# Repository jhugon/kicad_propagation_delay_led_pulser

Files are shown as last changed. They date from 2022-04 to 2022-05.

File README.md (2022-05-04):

# Propagation Delay LED Pulser Board in KiCAD

This KiCad board pulses an LED with a very short pulse. The pulse width is
defined by the propagation delay of 3 inverters.

Main power supply: 5 V

LED bias: 0-1.4 V, lower is brighter

## Changelog

- v1.0 Difficult to hand-solder due to heat loss to ground plane (too many vias) and reversed 0612 capacitors
- v1.1 Remove extra vias and switch from 0612 to 1206 coupling caps

## Performance

### v1.1

Measured on 2022-05-04

Current draw not visible on power supply, so less than 10 mA

All measured with a 10x passive oscilloscope probe and ground clib hooked up to coax out:

- The clock coming out of the timer: 9.36 kHz
- The pulse coming out of the NAND gate:
  - Rise and fall times of 2 ns (may be probes)
  - Width of 11 ns
  - Baseline is 4.8 V
  - Pulse is 8 mV
- The pulse coming out of the coax driving inverters, going into R2:
  - A fair amount of ringing ~ 20%
  - Rise and fall times of 2 ns (see above)
  - Width of 11 ns
  - Baseline is -77 mV
  - Pulse is 5 V
- The LED anode:
  - Rise time: 2 ns
  - Fall time: ringing 8.5 ns
  - Width: 12 ns
  - Baseline: -77 mV
  - Pulse: 2.8 V

Pulse measurement of coax output into high-Z scope input:

- Rise time 2.48 ns
- Fall time 2.45 ns
- Width 11.61 ns
- Baseline -90 mV
- Pulse 4.6 V
- Ringing ~ 10%, damped out around 20 ns after pulse fall

LED pulse measurements return a signal as expected at 9.36 kHz. The signal is
controllable with the bias voltage. Noise seems high, but that may be something
else

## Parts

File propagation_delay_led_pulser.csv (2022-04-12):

Source: | /home/jhugon/kicad/propagation_delay_led_pulser/propagation_delay_led_pulser.kicad_sch
Date: | Tue 12 Apr 2022 01:35:03 PM CDT
Tool: | Eeschema 6.0.4-6f826c9f35~116~ubuntu20.04.1
Generator: | /usr/share/kicad/plugins/bom_csv_grouped_by_value.py
Component Count: | 15
Individual Components:
Item | Qty | Reference(s) | Value | LibPart | Footprint | Datasheet | Mfr | Part
 |  | C1 | 22u | Device:C | Capacitor_SMD:C_1206_3216Metric_Pad1.33x1.80mm_HandSolder | https://www.mouser.com/datasheet/2/585/MLCC-1837944.pdf | Samsung | CL31A226KAHNNNE
 |  | C2 | 1n | Device:C | Capacitor_SMD:C_1206_3216Metric_Pad1.33x1.80mm_HandSolder | https://www.mouser.com/datasheet/2/40/C0GNP0_Dielectric-951274.pdf | Kyocera AVX | 12063A102FAT2A
 |  | C3 | 0.1u | Device:C | Capacitor_SMD:C_1206_3216Metric_Pad1.33x1.80mm_HandSolder | https://www.mouser.com/datasheet/2/585/MLCC-1837944.pdf | Samsung | CL31B104KBCNNND
 |  | C4 | 0.1u | Device:C | Capacitor_SMD:C_1206_3216Metric_Pad1.33x1.80mm_HandSolder | https://www.mouser.com/datasheet/2/585/MLCC-1837944.pdf | Samsung | CL31B104KBCNNND
 |  | C5 | 0.1u | Device:C | Capacitor_SMD:C_1206_3216Metric_Pad1.33x1.80mm_HandSolder | https://www.mouser.com/datasheet/2/585/MLCC-1837944.pdf | Samsung | CL31B104KBCNNND
 |  | C6 | 1u | Device:C | Capacitor_SMD:C_1206_3216Metric_Pad1.33x1.80mm_HandSolder | https://www.mouser.com/datasheet/2/585/MLCC-1837944.pdf | Samsung | CL31B105KBHNFNE
 |  | D1 | LED | Device:LED | LED_SMD:LED_1206_3216Metric_Pad1.42x1.75mm_HandSolder | https://www.mouser.com/datasheet/2/239/Lite-On-LTST-C150TBKT-1175371.pdf | Lite-On | LTST-C150TBKT
 |  | J1 | Power/Bias In | Connector_Generic:Conn_02x02_Top_Bottom | Connector_Molex:Molex_Nano-Fit_105314-xx04_2x02_P2.50mm_Horizontal | https://www.mouser.com/datasheet/2/276/4/1053141304_PCB_HEADERS-2883302.pdf | Molex | 1053141304
 |  | J2 | Pulse Out | Connector:Conn_Coaxial | Connector_Coaxial:SMA_Amphenol_132289_EdgeMount | https://www.mouser.com/datasheet/2/18/1/amphs06501_1-2259276.pdf | Amphenol RF | 132289
 |  | R1 | 72K | Device:R_US | Resistor_SMD:R_1206_3216Metric_Pad1.30x1.75mm_HandSolder | https://www.mouser.com/datasheet/2/427/dcrcwe3-1762152.pdf | Vishay | CRCW120671K5FKEA
 |  | R2 | 50R | Device:R_US | Resistor_SMD:R_1206_3216Metric_Pad1.30x1.75mm_HandSolder | https://www.mouser.com/datasheet/2/427/crcwce3-1762584.pdf | Vishay | CRCW120649R9FKEAC
 |  | R3 | 50R | Device:R_US | Resistor_SMD:R_1206_3216Metric_Pad1.30x1.75mm_HandSolder | https://www.mouser.com/datasheet/2/427/crcwce3-1762584.pdf | Vishay | CRCW120649R9FKEAC
 |  | U1 | 74AC14 | 74xx:74HC14 | Package_SO:SOIC-14_3.9x8.7mm_P1.27mm | https://www.ti.com/lit/ds/symlink/sn74ac14.pdf | Texas Instruments | SN74AC14D
 |  | U2 | ICM7555xB | Timer:ICM7555xB | Package_SO:SOIC-8_3.9x4.9mm_P1.27mm | http://www.intersil.com/content/dam/Intersil/documents/icm7/icm7555-56.pdf | Maxim | ICM7555ESA+
 |  | U3 | 74AHC1G00 | 74xGxx:74AHC1G00 | Package_TO_SOT_SMD:SOT-23-5_HandSoldering | http://www.ti.com/lit/sg/scyt129e/scyt129e.pdf | Texas Instruments | SN74AHC1G00DBV
Collated Components:
Item | Qty | Reference(s) | Value | LibPart | Footprint | Datasheet | Mfr | Part
1 | 1 | C1 | 22u | Device:C | Capacitor_SMD:C_1206_3216Metric_Pad1.33x1.80mm_HandSolder | https://www.mouser.com/datasheet/2/585/MLCC-1837944.pdf | Samsung | CL31A226KAHNNNE
2 | 1 | C2 | 1n | Device:C | Capacitor_SMD:C_1206_3216Metric_Pad1.33x1.80mm_HandSolder | https://www.mouser.com/datasheet/2/40/C0GNP0_Dielectric-951274.pdf | Kyocera AVX | 12063A102FAT2A
3 | 3 | C3, C4, C5 | 0.1u | Device:C | Capacitor_SMD:C_1206_3216Metric_Pad1.33x1.80mm_HandSolder | https://www.mouser.com/datasheet/2/585/MLCC-1837944.pdf | Samsung | CL31B104KBCNNND
4 | 1 | C6 | 1u | Device:C | Capacitor_SMD:C_1206_3216Metric_Pad1.33x1.80mm_HandSolder | https://www.mouser.com/datasheet/2/585/MLCC-1837944.pdf | Samsung | CL31B105KBHNFNE
5 | 1 | D1 | LED | Device:LED | LED_SMD:LED_1206_3216Metric_Pad1.42x1.75mm_HandSolder | https://www.mouser.com/datasheet/2/239/Lite-On-LTST-C150TBKT-1175371.pdf | Lite-On | LTST-C150TBKT
6 | 1 | J1 | Power/Bias In | Connector_Generic:Conn_02x02_Top_Bottom | Connector_Molex:Molex_Nano-Fit_105314-xx04_2x02_P2.50mm_Horizontal | https://www.mouser.com/datasheet/2/276/4/1053141304_PCB_HEADERS-2883302.pdf | Molex | 1053141304
7 | 1 | J2 | Pulse Out | Connector:Conn_Coaxial | Connector_Coaxial:SMA_Amphenol_132289_EdgeMount | https://www.mouser.com/datasheet/2/18/1/amphs06501_1-2259276.pdf | Amphenol RF | 132289
8 | 1 | R1 | 72K | Device:R_US | Resistor_SMD:R_1206_3216Metric_Pad1.30x1.75mm_HandSolder | https://www.mouser.com/datasheet/2/427/dcrcwe3-1762152.pdf | Vishay | CRCW120671K5FKEA
9 | 2 | R2, R3 | 50R | Device:R_US | Resistor_SMD:R_1206_3216Metric_Pad1.30x1.75mm_HandSolder | https://www.mouser.com/datasheet/2/427/crcwce3-1762584.pdf | Vishay | CRCW120649R9FKEAC
10 | 1 | U1 | 74AC14 | 74xx:74HC14 | Package_SO:SOIC-14_3.9x8.7mm_P1.27mm | https://www.ti.com/lit/ds/symlink/sn74ac14.pdf | Texas Instruments | SN74AC14D
11 | 1 | U2 | ICM7555xB | Timer:ICM7555xB | Package_SO:SOIC-8_3.9x4.9mm_P1.27mm | http://www.intersil.com/content/dam/Intersil/documents/icm7/icm7555-56.pdf | Maxim | ICM7555ESA+
12 | 1 | U3 | 74AHC1G00 | 74xGxx:74AHC1G00 | Package_TO_SOT_SMD:SOT-23-5_HandSoldering | http://www.ti.com/lit/sg/scyt129e/scyt129e.pdf | Texas Instruments | SN74AHC1G00DBV

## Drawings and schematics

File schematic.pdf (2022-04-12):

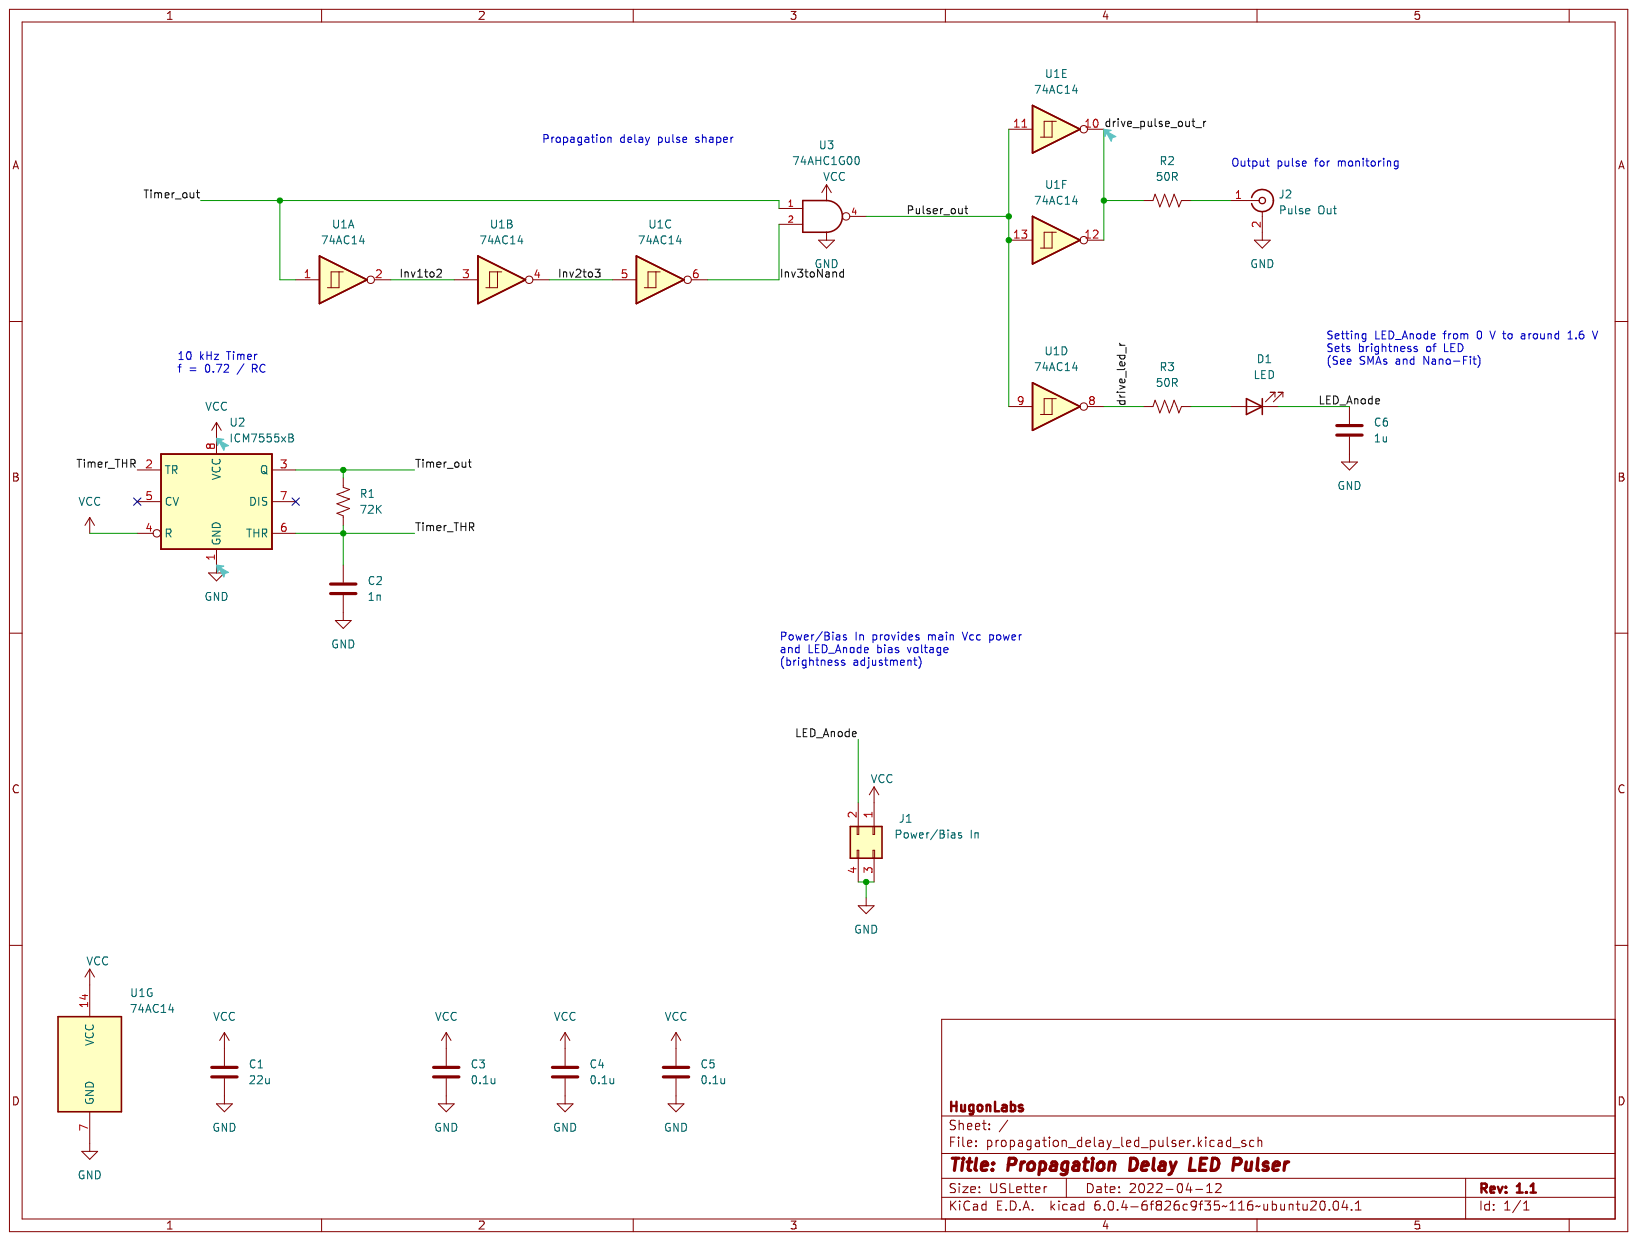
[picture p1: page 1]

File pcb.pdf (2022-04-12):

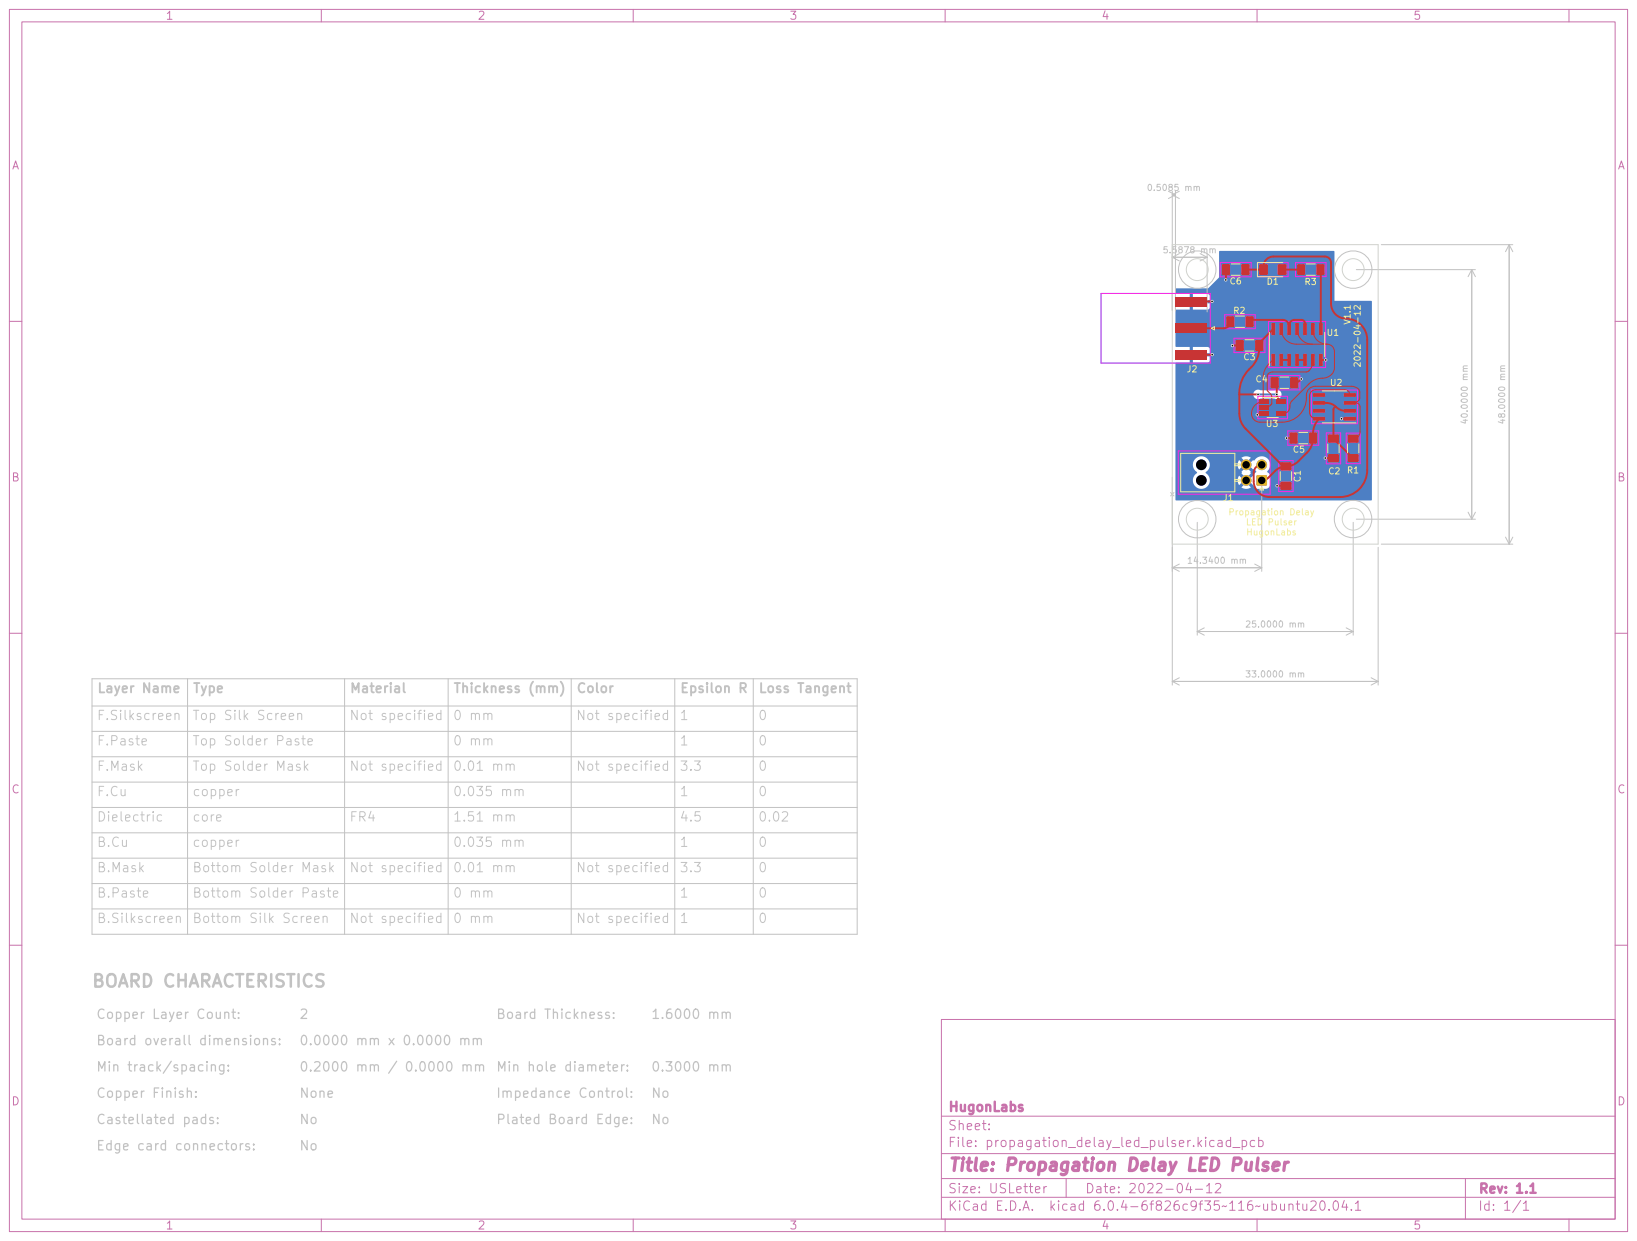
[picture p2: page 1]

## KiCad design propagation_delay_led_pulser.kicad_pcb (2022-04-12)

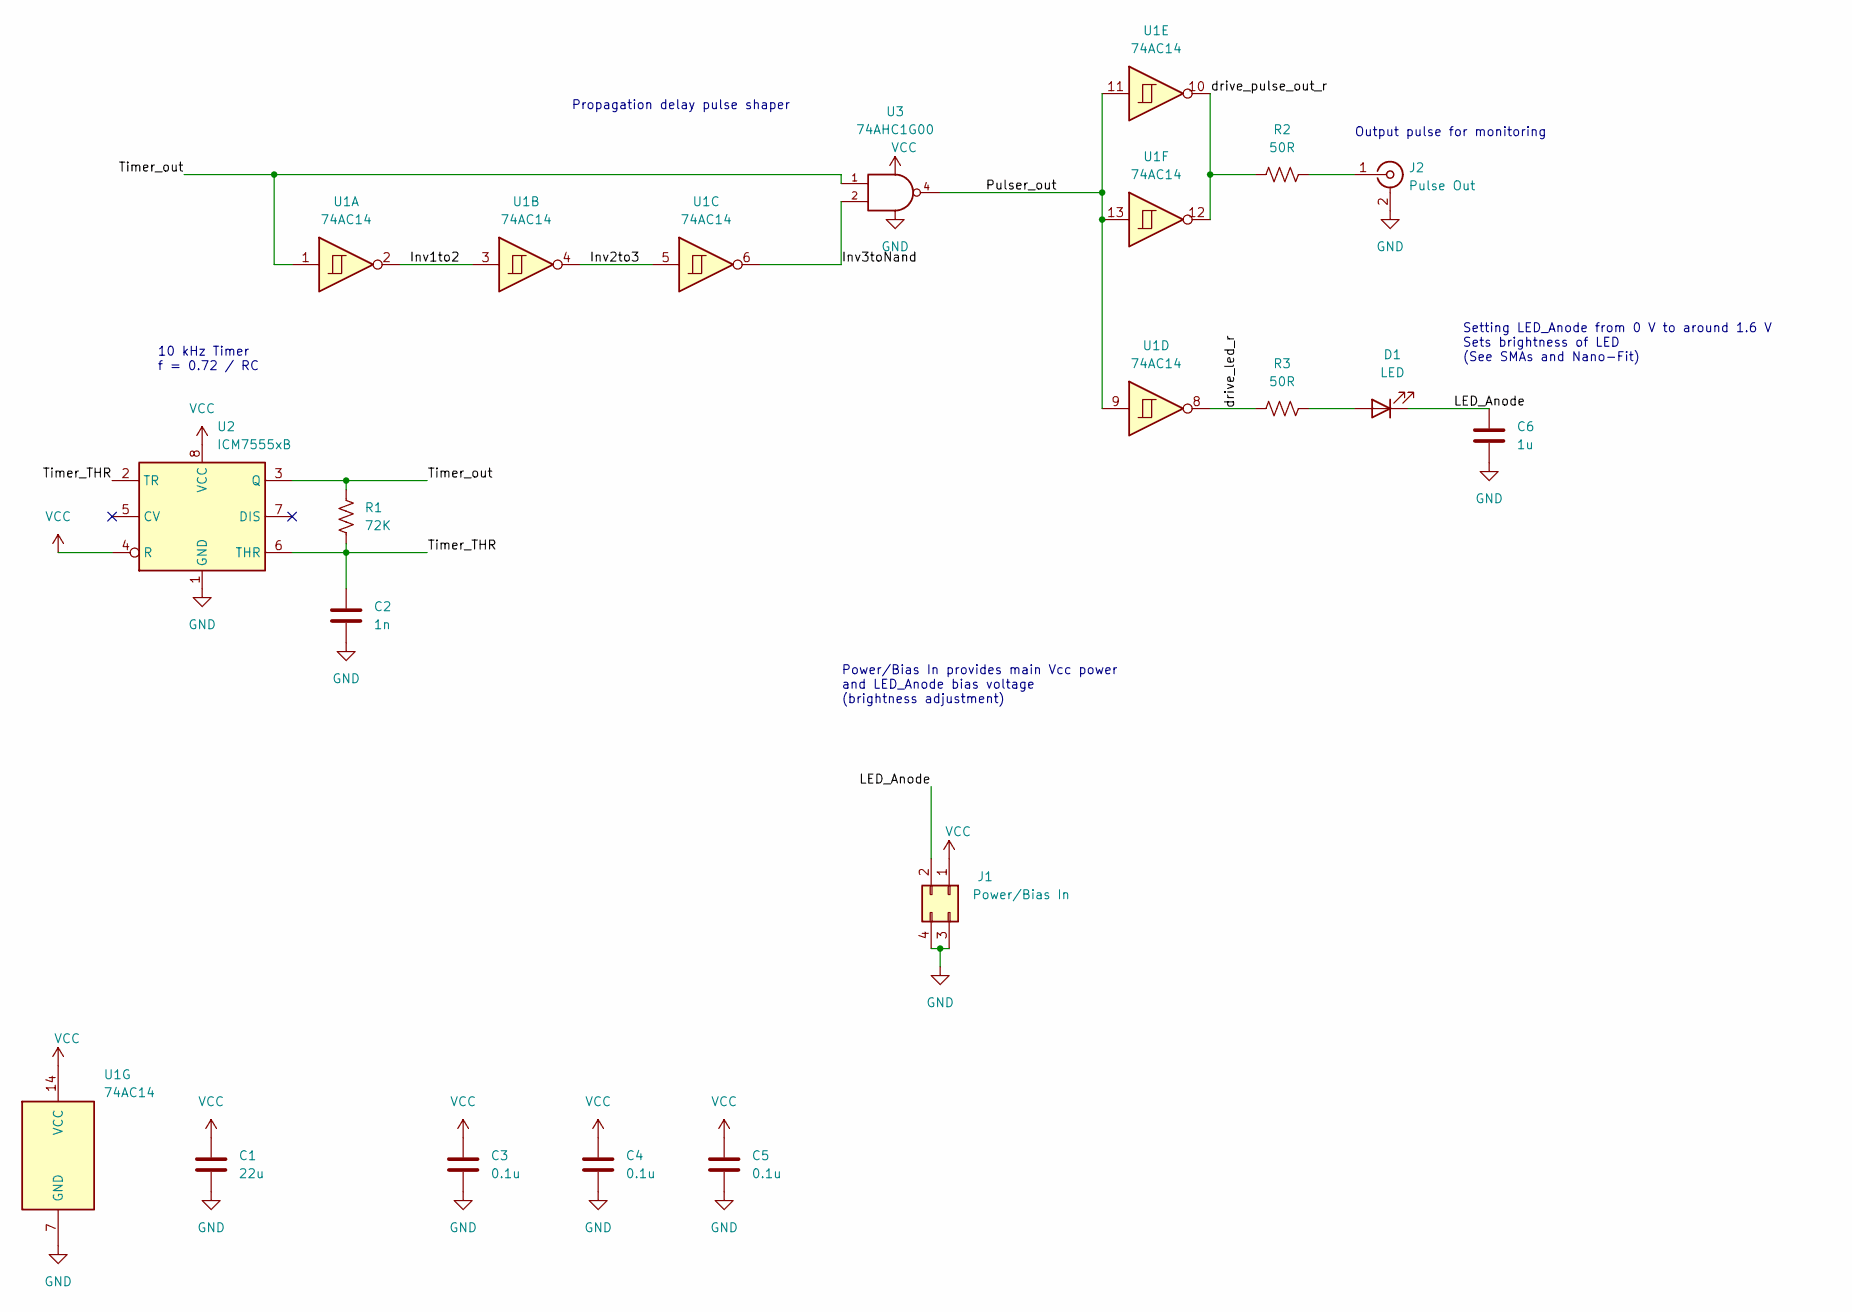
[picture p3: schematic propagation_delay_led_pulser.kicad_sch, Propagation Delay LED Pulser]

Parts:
C1: 22u; C_1206_3216Metric_Pad1.33x1.80mm_HandSolder; Part CL31A226KAHNNNE
C2: 1n; C_1206_3216Metric_Pad1.33x1.80mm_HandSolder; Part 12063A102FAT2A
C3, C4, C5: 0.1u; C_1206_3216Metric_Pad1.33x1.80mm_HandSolder; Part CL31B104KBCNNND
C6: 1u; C_1206_3216Metric_Pad1.33x1.80mm_HandSolder; Part CL31B105KBHNFNE
D1: LED; LED_1206_3216Metric_Pad1.42x1.75mm_HandSolder; Part LTST-C150TBKT
J1: Power/Bias In; Molex_Nano-Fit_105314-xx04_2x02_P2.50mm_Horizontal; Part 1053141304
J2: Pulse Out; SMA_Amphenol_132289_EdgeMount; Part 132289
R1: 72K; R_1206_3216Metric_Pad1.30x1.75mm_HandSolder; Part CRCW120671K5FKEA
R2, R3: 50R; R_1206_3216Metric_Pad1.30x1.75mm_HandSolder; Part CRCW120649R9FKEAC
U1: 74AC14; SOIC-14_3.9x8.7mm_P1.27mm; Part SN74AC14D
U2: ICM7555xB; SOIC-8_3.9x4.9mm_P1.27mm; Part ICM7555ESA+
U3: 74AHC1G00; SOT-23-5_HandSoldering; Part SN74AHC1G00DBV

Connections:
/Inv1to2: U1.2, U1.3
/Inv2to3: U1.4, U1.5
/Inv3toNand: U1.6, U3.2
/LED_Anode: C6.1, D1.1 (K), J1.2
/Pulser_out: U1.9, U1.11, U1.13, U3.4
/Timer_THR: C2.1, R1.2, U2.2 (TR), U2.6 (THR)
/Timer_out: R1.1, U1.1, U2.3 (Q), U3.1
/drive_led_r: R3.1, U1.8
/drive_pulse_out_r: R2.1, U1.10, U1.12
GND: C1.2, C2.2, C3.2, C4.2, C5.2, C6.2, J1.3, J1.4, J2.2 (Ext), U1.7 (GND), U2.1 (GND), U3.3 (GND)
unnamed: D1.2 (A), R3.2
unnamed: J2.1 (In), R2.2
VCC: C1.1, C3.1, C4.1, C5.1, J1.1, U1.14 (VCC), U2.4 (R), U2.8 (VCC), U3.5 (VCC)

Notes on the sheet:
Output pulse for monitoring
Setting LED_Anode from 0 V to around 1.6 V Sets brightness of LED (See SMAs and Nano-Fit)
Propagation delay pulse shaper
10 kHz Timer f = 0.72 / RC
Power/Bias In provides main Vcc power and LED_Anode bias voltage (brightness adjustment)

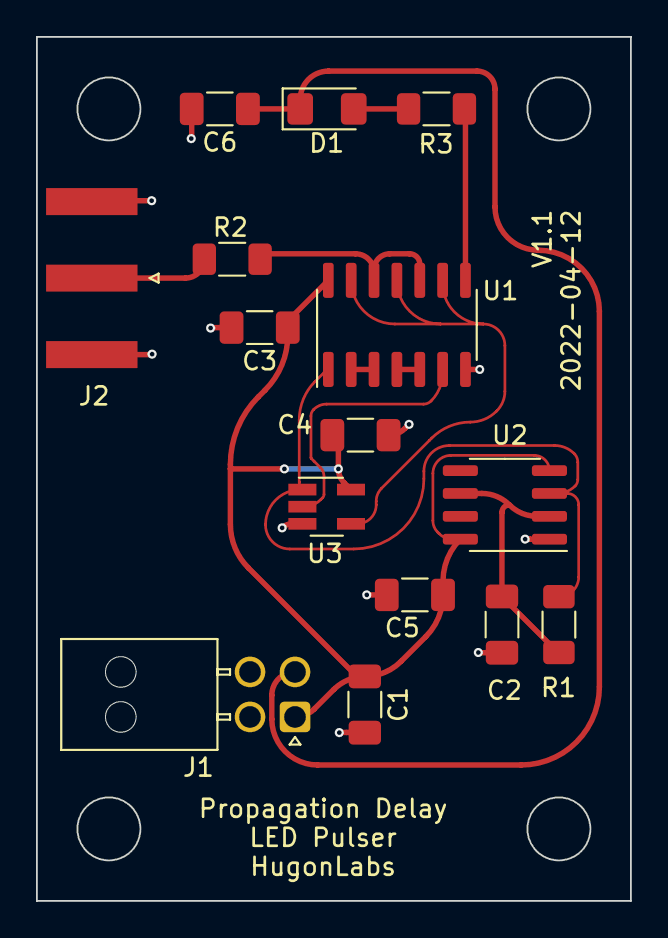
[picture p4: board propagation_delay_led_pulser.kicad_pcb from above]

Board: 2 copper layers, 33.0 x 48.0 mm, 15 parts (0 on the bottom side), 13 nets.

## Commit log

2022-02-27 Switched to 555 for timer
    [propagation_delay_led_pulser.csv, propagation_delay_led_pulser.kicad_sch]
2022-02-28 Changed headers to one nano-fit
    [propagation_delay_led_pulser.csv, propagation_delay_led_pulser.kicad_pcb, propagation_delay_led_pulser.kicad_sch]
2022-02-28 removed pwr/bias SMAs and initial PCB placement
    also added mfr/part for timer capacitor
    [propagation_delay_led_pulser.csv, propagation_delay_led_pulser.kicad_pcb, propagation_delay_led_pulser.kicad_sch]
2022-02-28 Added board outline
    aligned connectors with outline
    added power for inverter to schematic
    [propagation_delay_led_pulser.csv, propagation_delay_led_pulser.kicad_pcb, propagation_delay_led_pulser.kicad_sch]
2022-02-28 most routing done, need to poar ground plane
    [propagation_delay_led_pulser.csv, propagation_delay_led_pulser.kicad_pcb, propagation_delay_led_pulser.kicad_sch]
2022-02-28 PCB layout complete
    [propagation_delay_led_pulser.csv, propagation_delay_led_pulser.kicad_pcb, propagation_delay_led_pulser.kicad_sch]
2022-02-28 Generated Gerbers for v1
    [propagation_delay_led_pulser-B_Cu.gbl, propagation_delay_led_pulser-B_Mask.gbs, propagation_delay_led_pulser-B_Paste.gbp, propagation_delay_led_pulser-B_Silksc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]
2022-04-12 Removed extra vias and changed 0612 caps to 1206
    should ease soldering greatly
    Hopefully all done for v1.1
    [propagation_delay_led_pulser.csv, propagation_delay_led_pulser.kicad_pcb, propagation_delay_led_pulser.kicad_sch]
2022-04-12 generated v1.1 gerbers
    successfully uploaded to manufacturer
    [propagation_delay_led_pulser-B_Cu.gbl, propagation_delay_led_pulser-B_Mask.gbs, propagation_delay_led_pulser-B_Paste.gbp, propagation_delay_led_pulser-B_Silksc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]
